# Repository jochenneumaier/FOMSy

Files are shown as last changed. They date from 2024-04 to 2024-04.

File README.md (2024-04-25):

# FOMSy
A 3D-Printed Flexible Open-Source Microfluidic System, containing a double syringe pump, pressure sensor and back pressure regulator

In this work, we introduce a low-cost open-source flow system that includes a dual syringe pump with implemented pressure sensor and back pressure regulator. The entire system can be built for around 500 €. Commercially available flow systems can be very expensive with equipment starting at, but often greatly exceeding, 10,000 €. This high price of entry makes such technology prohibitively expensive for many research groups. Such systems stand to benefit the emerging academic pharmaceutical field by providing the experience and availability of reliable and affordable solutions. To implement accessible flow chemistry at research facilities, the systems must be made affordable. In addition, space in research laboratories is usually limited and commercially available flow systems can be very bulky. Having a compact and individually adjustable system is thus beneficial, with 3D printing technology offering the solution. Our compact 3D-printed system meets the needs of many applications in flow chemistry research as well as educational requirements for universities. As a proof of concept, we conceptualized, developed, and tested a custom flow system that can be used to synthesize [18F]2-fluoro-2-desoxy-d-glucose ([18F]FDG), the most commonly used PET-tracer. This system was designed to perform the typical functions and operations required in radiotracer production i.e. radiofluorination, dilution, SPE-trapping, deprotection, and SPE-elution. With this proof-of-concept in hand, the system can be easily customized to produce other radiopharmaceuticals.

graphical abstract

The work was published in the Journal of Flow Chemistry and can be viewed here:

FOMSy: 3D-printed flexible open-source microfluidic system and flow synthesis of PET-tracer. F. Menzel, J. Cotton, T. Klein, A. Maurer, T. Ziegler, J. M. Neumaier, J. Flow Chem. 2023, https://doi.org/10.1007/s41981-023-00267-z

https://link.springer.com/content/pdf/10.1007/s41981-023-00267-z.pdf

A detailed assembly instructions can also be downloaded here:

https://static-content.springer.com/esm/art%3A10.1007%2Fs41981-023-00267-z/MediaObjects/41981_2023_267_MOESM1_ESM.pdf

All CAD and stl files as well as the Arduino and Nextion program codes can be downloaded here:

https://static-content.springer.com/esm/art%3A10.1007%2Fs41981-023-00267-z/MediaObjects/41981_2023_267_MOESM2_ESM.zip

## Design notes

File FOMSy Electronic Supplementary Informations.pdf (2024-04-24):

## Electronic Supplementary Informations

## FOMSy: 3D-Printed Flexible Open-Source Microfluidic System and Flow Synthesis of PET-Tracer

Florian Menzela,b, Jonathan Cottonb,c, Thomas Kleina

, Andreas Maurerb,c, Thomas Zieglera and Jochen M. Neumaier*a

a
Institute of Organic Chemistry, University of Tuebingen, Auf der Morgenstelle 18, 72076 Tuebingen, Germany.
b | Werner Siemens Imaging Center, Department of Preclinical Imaging and Radiopharmacy,
| Eberhard Karls University, Tuebingen, Roentgenweg 15, 72076 Tuebingen, Germany
c | Cluster of Excellence iFIT “Image-Guided and Functionally Instructed Tumor Therapies“
| (EXC 2180), University of Tuebingen, 72076 Tuebingen, Germany

*E-Mail: jochen.neumaier@uni-tuebingen.de

Table of contents

3D printer setup

Two 3D printers were used for this work. 3D-printed parts out of PLA (polylactic acid) and

PETG (polyethylene terephthalate glycol-modified) were printed on an X-CF Pro from Qidi. 3D-

printed parts out of PEEK (Polyetheretherketone) were printed on an Apium P220 from Apium

Additive Technologies GmbH.

Software: All parts were designed with Autodesk Inventor Professional 2022. After modeling,

the files were exported as STL files and sliced with the software simplify3D.

PEEK parts: The parts out of PEEK were printed with Apium PEEK 4000 Natural filament with

an Apium P220 3D printer. The filament roll was dried in a vacuum oven at 80 °C and 50 mbar

overnight to ensure proper drying of the PEEK.

Print speed = 25 mm/s

Extrusion width: 0.40 mm

Extrusion multiplier = 0.90

Nozzle temp. = 480 °C

Bed temperature = 130 °C, glass plate coated with DimaFix pen with a brim of 24 perimeters

Layer height: 0.1 mm

PLA parts: PLA 1.75 mm from Janbex was used on the Qidi X-CF Pro 3D printer.

The following settings were used:

Print speed = 60 mm/s

Extrusion multiplier = 1.00

Nozzle temp. = 200 °C

Bed temperature = 60 °C, printed on a flexible metal PEI sheet, coated with DimaFix Spray or

pen.

Layer height: 0.2 mm – 0.3 mm

PETG parts: PETG 1.75 mm from Fiberlogy was used on the Qidi X-CF Pro 3D printer. The

filament roll was stored in a sealed box with silica gel bags inside to ensure proper drying of

the PETG.

The following settings were used:

Print speed = 60 mm/s

Extrusion multiplier = 1.00

Nozzle temp. = 230 °C

Bed temperature = 80 °C, printed on a flexible metal PEI sheet, coated with DimaFix Spray or

pen.

Layer height: 0.2 mm (if a part was printed with 0.3 mm layer height, it is indicated in the parts

list)

The STP and STL files of all printed parts can be found in the zip file “Data Files” in the

supplementary information. For more information also see our previous publications. [1], [2]

Dual syringe pump

All 3D-printed parts were printed in PLA (black) and PETG (bordeaux red). The exploded-view

CAD drawing of the syringe pump can be found in Figure S1, the single parts in Figure S2, and

the full parts list in Table S1.

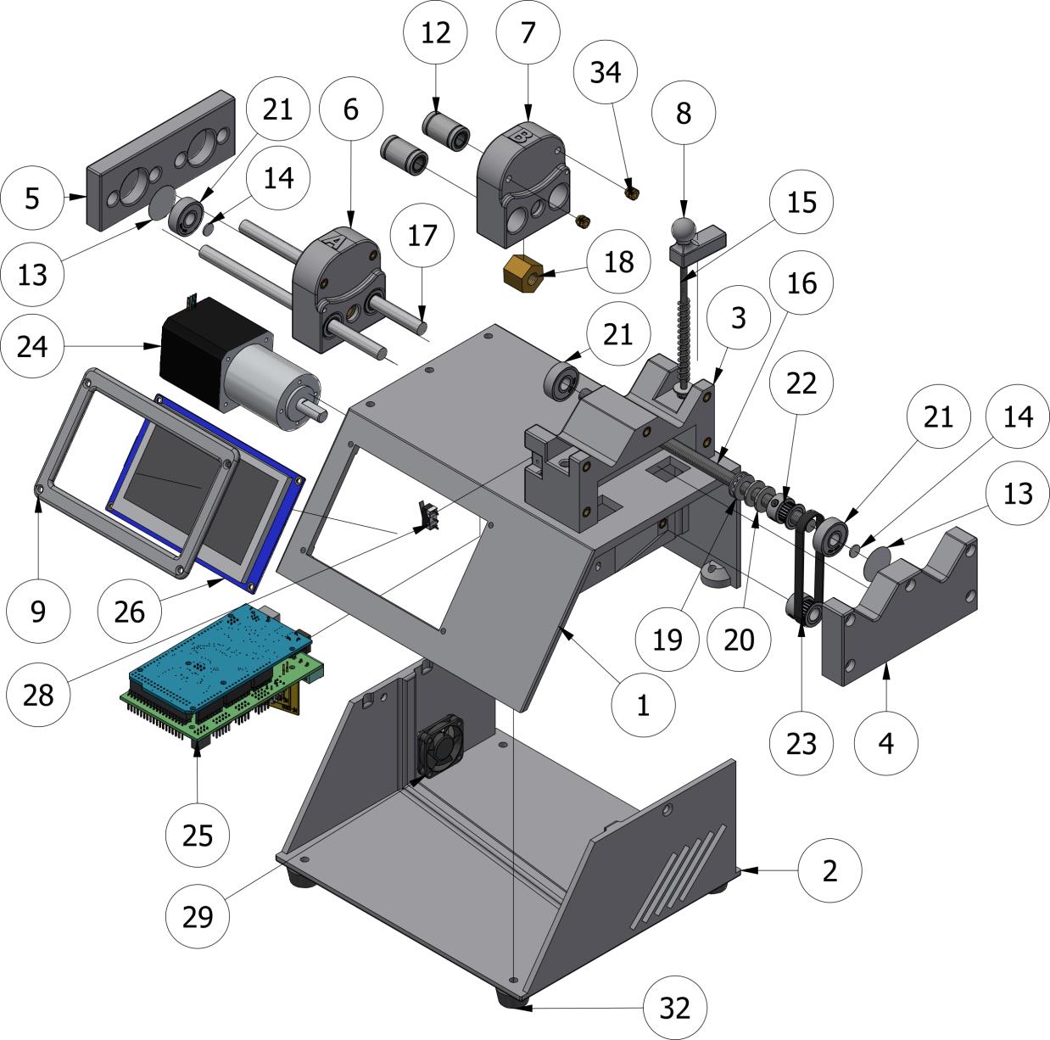
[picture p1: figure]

Figure S1: Exploded-view CAD drawings of the syringe pump.

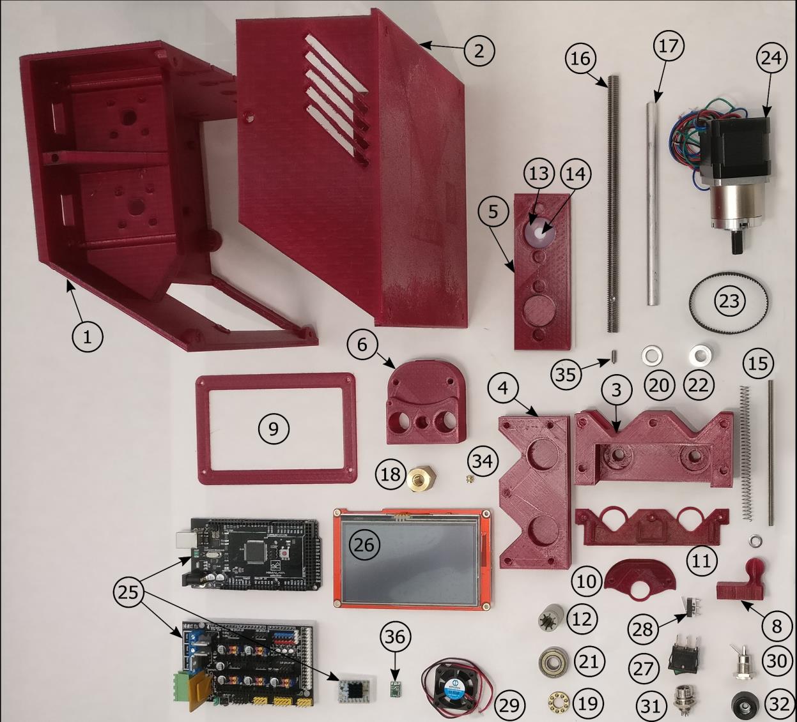
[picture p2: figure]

Figure S2: All 3D-printed, mechanical, and electronic parts with numbers.

Table S1: Parts list for the syringe pump. The screws and nuts that are needed for mounting

each part are given in brackets.

Quant. | Part | Source | No.
1 | Main pump body (printed with 0.3 mm layer height) | 3D-printed | 1
1 | Bottom part (printed with 0.3 mm layer height) | 3D-printed | 2
1 | Syringe holding block | 3D-printed | 3
1 | Front plate | 3D-printed | 4
1 | End plate | 3D-printed | 5
1 | Carrier block A | 3D-printed | 6
1 | Carrier block B | 3D-printed | 7
1 | Syringe clamp | 3D-printed | 8
1 | Display frame | 3D-printed | 9

Quant. | Part | Source | No.
2 | Syringe retainer back | 3D-printed | 10
1 | Syringe retainer front | 3D-printed | 11
4 | RJ4JP-01-08 drylin® R - bearing 8mm | Amazon | 12
4 | PTFE washer (22 mm × 0,1 mm) | In-house workshop | 13
4 | PTFE washer (8 mm × 2 mm) | In-house workshop | 14
2 | M4 Threaded rod | In-house workshop | 15.1
2 | compression spring 45 × 7 mm × 0.6 mm | In-house workshop | 15.2
2 | M4 locknut and washer, 12 mm | In-house workshop | 15.3
2 | Trapezoidal thread spindle, Tr8 × 1.5 × 185 mm | HFB-Gewindetechnik | 16
4 | Round rod, stainless steel, 8 × 145 mm | In-house workshop | 17
2 | Hexagon nut, Tr8 × 1.5 | HFB-Gewindetechnik | 18
2 | Thrust bearing, F8-16M 8 × 16 × 5mm | Amazon | 19
4 | Washer 8×16×15mm | In-house workshop | 20
6 | Ball bearing 608RS | Amazon | 21
4 | GT2 timing pulley, 8 mm bore, 20 teeth, for 6 mm belt | Amazon | 22
F4 | GT2 closed loop timing belt, 6 mm, 158 mm | Amazon | 23
2 | Nema 17 Stepper Motor Bipolar L=40mm w/ Gear Ratio 27:1 Planetary Gearbox | stepperonline | 24
1 | HIMALAYA basic MEGA 2560 | Eckstein GmbH | 25.1
1 | Ramps 1.4 controller | Eckstein GmbH | 25.2
3 | TMC2208 V1.2 stepper motor driver | Eckstein GmbH | 25.3
1 | Nextion NX4827T043 Display | Antratek Electronics | 26
1 | Rocker switch, 3-Pin | Eckstein GmbH | 27
2 | Pololu mini snap-action switch with 13.5mm lever | Eckstein GmbH | 28
1 | Cooling fan (30 × 30 × 10 mm), 5 V | Amazon | 29
1 | DC-socket 2.1/5.5mm | Reichelt elektronik GmbH & Co. KG | 30
1 | GX12 aviation socket, Pins 5 or 6 (+ aviation plug on the cable) | Amazon | 31
4 | Rubber feet, 20 × 9 mm | Amazon | 32
| Threaded inserts M4 × 8 or M4 × 6 | Amazon | 33
| Threaded inserts M3 × 6 | Amazon | 34
2 | Grub screw, M4 ×10 mm (ISO 4027) | In-house workshop | 35
1 | Pololu 5V Step-Up/Step-Down Voltage Regulator S9V11F5 | Eckstein GmbH | 36
| Hex Socket Head Cap Screws (ISO 4762), various sizes | In-house workshop | 37

Quant. | Part | Source | No.
| Hexagon socket countersunk screws (ISO 10642), various sizes | In-house workshop | 38
1 | Single output power supply 12 V, 3 A | Reichelt elektronik GmbH & Co. KG | 39
| jumper wire cables, female to female | Eckstein GmbH

Detailed step-by-step assembly instruction
In the following, a detailed assembly instruction with example photos is given. Together with

the exploded CAD view, it should be possible to assemble the pump without using special

tools. A bench drill with a vise is recommended in step 11 to drill an accurate hole.

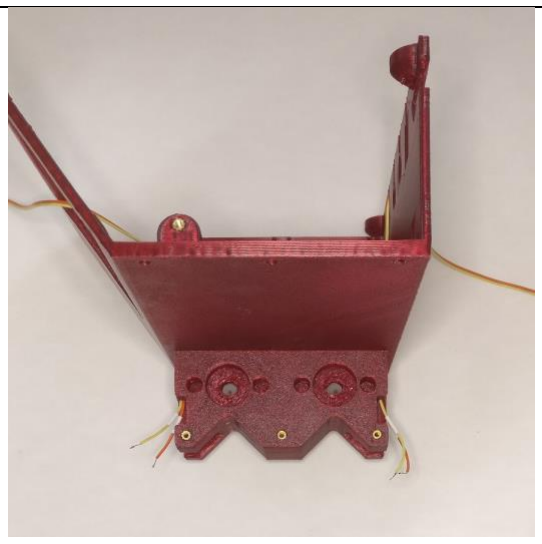
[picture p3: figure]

Step 1: All Threaded inserts (33 and 34) were inserted using a soldering iron Step 2: The two core wires for the end switch were pulled through the main pump body (1) and the syringe holding block (3). Step 3: The syringe holding block (3) was screwed (M4 head cap screws) on the main pump body (1).

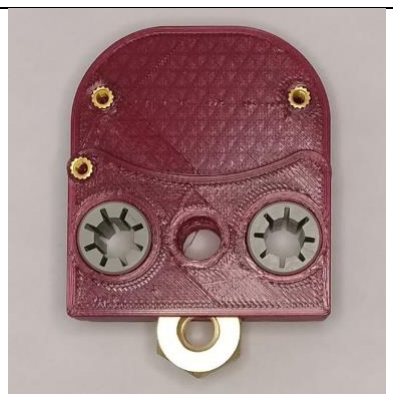
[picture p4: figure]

Step 4: The linear bearing (12) and the nut (18) were inserted into the carrier blocks A and B (6 and 7). Care should be taken that the round rod (17) runs without friction through the linear bearing! If not, increase the hole size of the carrier block.

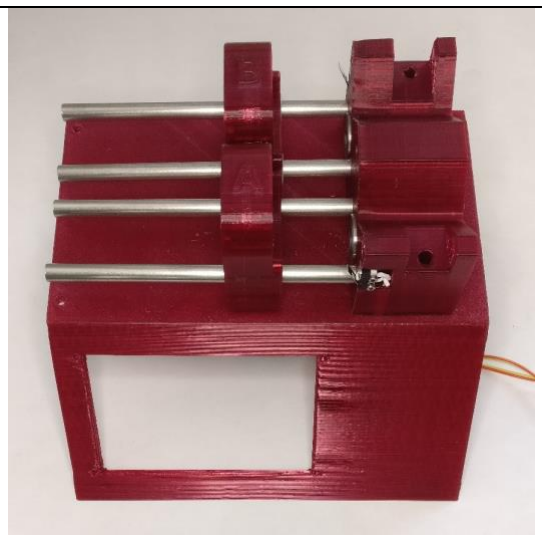
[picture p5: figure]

Step 5: The end switches (28) were soldered to the wires and attached to the syringe holding block. Step 6: The round rod (17) and two ball bearings (21) were inserted into the syringe holding block (3). Step 7: The two carrier blocks A and B (6 and 7) were slid in the round rods.
Step 8: The two 22 mm PTFE washers (13) and the two ball bearings (21) were inserted in the end plate (5). Step 9: The two 8 mm PTFE washers (14) were inserted into the two ball bearings (21).

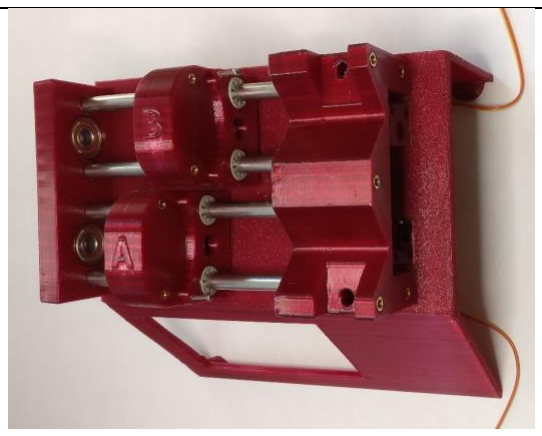
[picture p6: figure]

Step 10: The end plate (5) was screwed (M4 head cap screws) to the main pump body (1). Care should be taken that the carrier blocks move without friction!

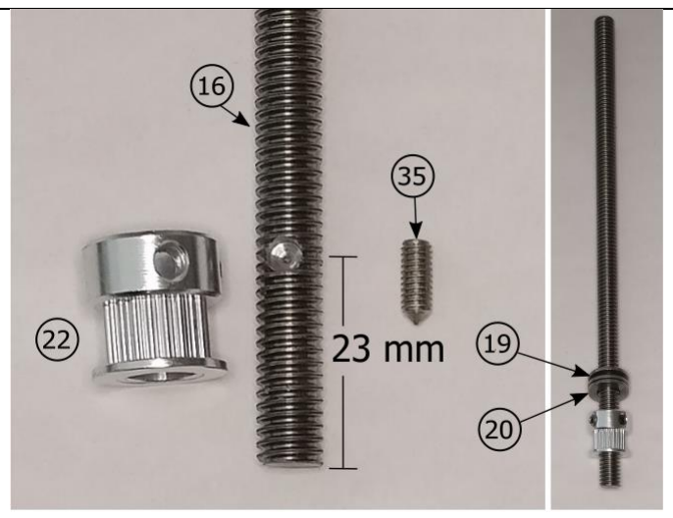
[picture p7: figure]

Step 11: A hole (4mm) was drilled halfway through the trapezium thread spindle (16) with a distance of 23 mm from center to end (bench drill with a vise is recommended). Step 12: The timing pulley (22) was screwed to the threaded spindle with a grub screw (35). Step 13: Two washers (20) and the thrust bearing (19) were attached (total thickness of 8mm).

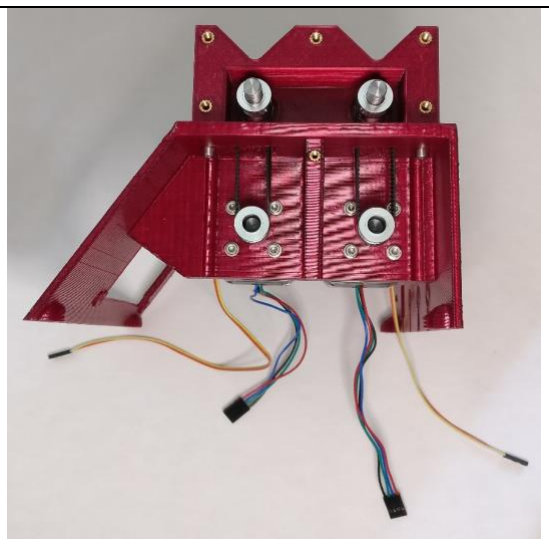
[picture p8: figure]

Step 14: The spindles from step 13 were inserted. Make sure that the spindle can be rotated without much resistance! Step 15: The gear stepper motors (24) were loosely attached (M3 head cap screws with washers) to the main pump body (1). Step 16: The timing pulleys (22) and the timing belts (23) were attached. The timing belts were put under tension and the motors and pulleys were tightened firmly.

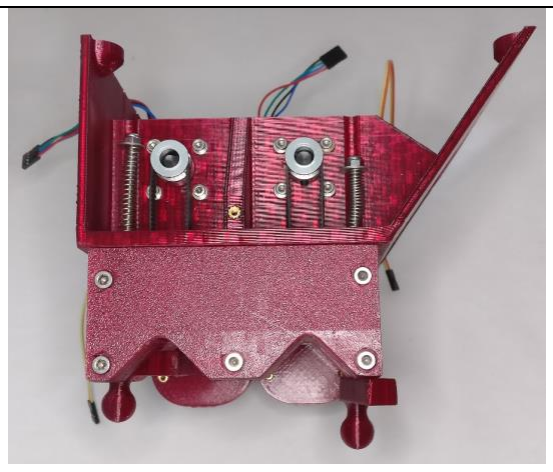
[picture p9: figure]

Step 17: The front plate (4) was screwed (M4 head cap screws) to the pump. Step 18: The M4 threaded rods (15.1) were screwed into the syringe clamps (8) and inserted through the holes. Step 19: The compression spring (15.2) was inserted and fixed with the washer and lock nut.
Step 20 (optional): A second 5 V output was soldered to the Voltage Regulator (36). This could be used to supply power to the sensor module if no motorized BPR is used! If a separate power supply on the sensor module is used, do not connect power from pump to sensor!

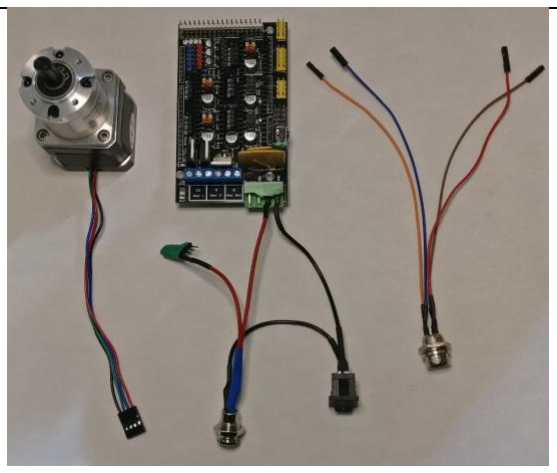
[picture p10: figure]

Step 21: The cables of the motors were shortened and connected to a 4-pin plug (black – green – blue – red). Step 22: Cables were soldered (see figure S3) to the components (27, 30, 31, 36). The 12 V (+ and -) input cable was soldered directly to the RAMPS controller (25.2) The voltage regulator (36) should be encased in heat shrink tubing to prevent accidental electrical contact with other parts.

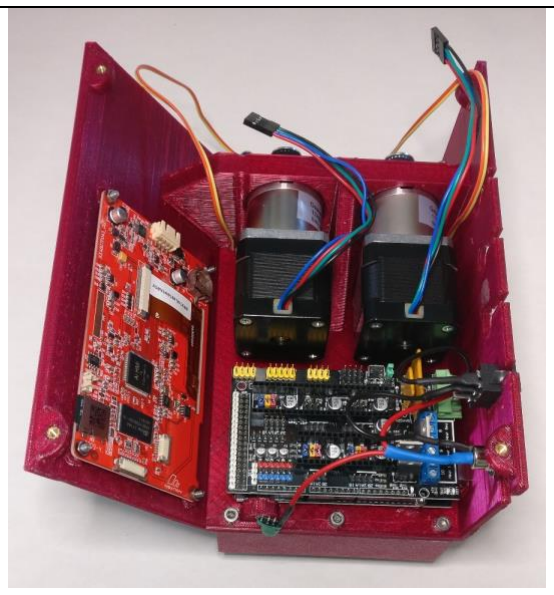
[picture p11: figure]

Step 23: The Arduino Mega (25.1) was screwed (M3 head cap screws) to the Main pump body (1). Step 24: The electronic part from step 22 was attached to the main pump body. The RAMPS controller (25.2) was plugged on the Arduino. Step 25: The Nextion display (26) was screwed (M3 countersunk screws with M3 nuts) with the display frame (9) to the main pump body.
Step 26: The TMC2208 stepper motor drivers (25.3) were plugged on the RAMPS (Jumper to MS2, middle position). Step 27: The wires were connected as described in Figure S3.
Step 28: The cooling fan was screwed (M3 countersunk screws with M3 nuts) to the bottom part (2)

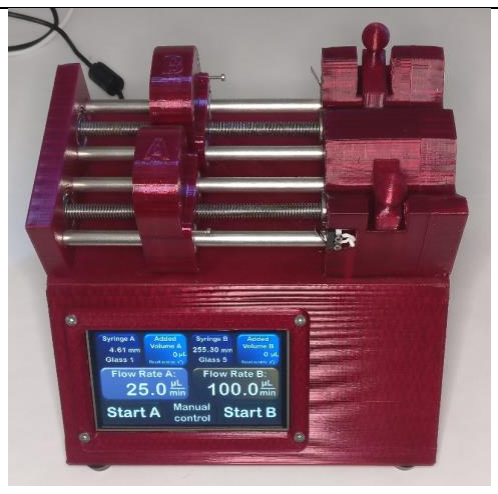
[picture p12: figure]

Step 29: The bottom part (2) with the rubber feet (32) was screwed (M3 countersunk and head cap screws) to the main pump body (1). PLA version of the pump:

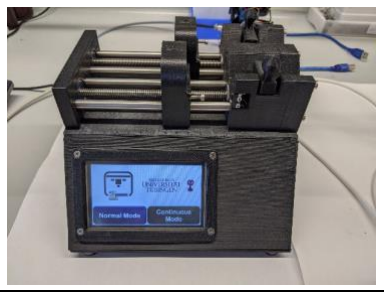
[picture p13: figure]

Optional: Syringe retainers (10 and 11) can be used to hold the syringes in place when drawing up a solution into the syringe using the motors.
The syringe retainers must be adjusted for each syringe itself so that it fits optimally (change hole diameter and thickness).
The uploaded retainers are optimized for a Hamilton 5 mL Gastight Syringe Model 1005

Electronic setup of the pump
For controlling the motors of the pump an Arduino Mega 2560 was used with a RAMPS 1.4

controller shield attached. TMC2208 stepper motor driver was connected to the RAPMS

controller at X and Y positions and the jumper settings were set to 1/4 microsteps (jumper on

MS2, middle position). The current limiting was adjusted on the TMC2208 stepper motor

driver to around 2.4 A with the integrated trimmer potentiometer (1.2 V). For a constant

voltage of 5 V for the Nextion Display, a Pololu S9V11F5 5 V Step-Up/Step-Down Voltage

Regulator was used. The RAMPS controller was connected to a standard 12 V DC, 3 A power

supply over a rocker switch, and a DC socket. The detailed assignment of the electronics is

shown in Figure S3. All electronic parts were connected using standard female-to-female or

female-to-male jumper wires.

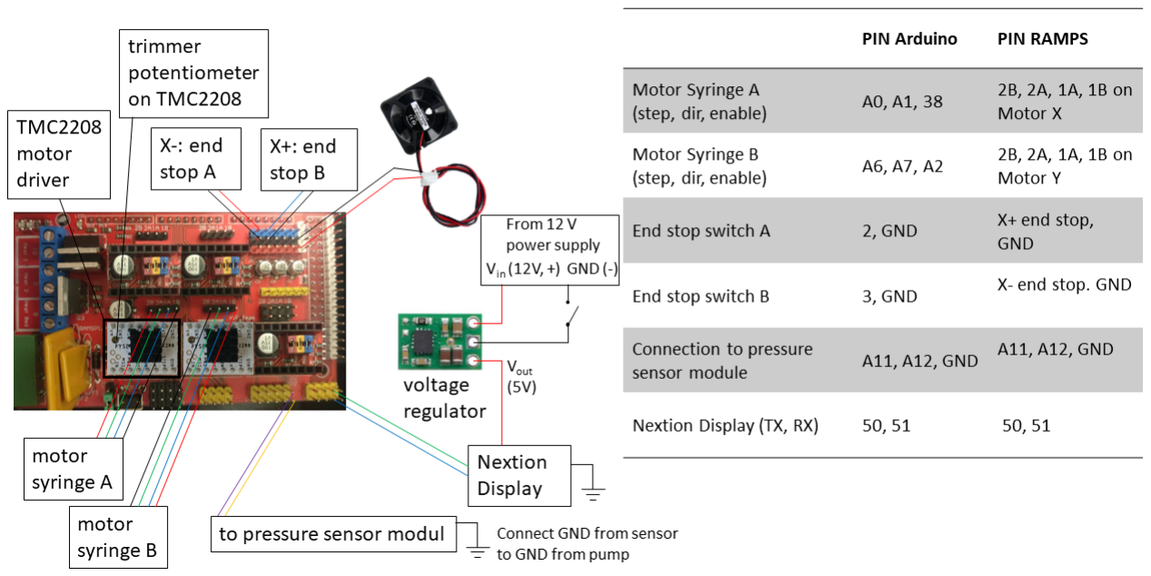
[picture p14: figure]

Figure S3: Wiring diagram of the Arduino with PIN assignment.

Programming with Arduino and Nextion software: The software was written on the open-

source Arduino software (Ver. 1.8.15) and the Nextion Editor (Ver. 1.63.3.). The codes can be

downloaded from the supplementary files. In the software, five Hamilton gastight syringes

and five disposable syringes were implemented. The diameters of these syringes were taken

from the corresponding company’s website. Detailed Information (company, diameter,

accuracy) can be found in Table S2. For changing the syringes to other predefined syringes,

the Nextion code on pages “syA” and “syB” has to be edited. The text in the buttons b0 – b9

could be changed to the corresponding value in the attribute window (change txt). The

diameter of new syringes has to be edited in the event window. An example is given here:

Old syringe | New syringe | Changes

n1.val=4

t13.txt="69"

main.t5.txt="Plastic 1"

n1.val=6

t13.txt="12"

main.t5.txt="Metal 1"

The diameter was changed from 4.69 mm

to 6.12 mm. The name, which appears on

the main page, was changed from Plastic

1 to Metal 1.

Accuracy test of the syringe pump: Each kind of pre-programmed syringes were tested with

typical flow rates for continuous flow reactions. Distilled water was dispensed at room

temperature for 1 to 10 min and the measured weight was compared to the theoretical

weight.

Table S2: Accuracy test of the pre-programmed syringes.

Volume | Syringe | Flow rate [µL/min] | Time [min] | Weight [g] | Deviation [%]
1 mL | HSW NORM-JECT® | 100 50 10 5 1 | 5 10 20 30 50 | 0.498 0.497 0.197 0.147 0.048 | 0.08 0.29 1.52 1.78 3.47

Volume | Syringe | Flow rate [µL/min] | Time [min] | Weight [g] | Deviation [%]
2 mL | BD Discardit II | 200 100 20 10 2 | 5 10 20 30 50 | 0.995 0.995 0.397 0.295 0.098 | 0.27 0.30 0.42 1.54 2.09
5 mL | BD Discardit II | 500 250 50 25 5 | 5 10 20 30 50 | 2.474 2.481 0.993 0.737 0.243 | 0.81 0.50 0.44 1.56 2.53
10 mL | HSW NORM-JECT® | 1000 500 100 50 10 | 5 10 20 30 50 | 4.970 4.961 1.987 1.474 0.488 | 0.34 0.53 0.40 1.48 2.18
20 mL | BD Discardit II | 2000 1000 200 100 20 | 5 10 20 30 50 | 9.897 9.913 3.972 2.928 0.973 | 0.78 0.62 0.46 2.21 2.49
0.1 mL | Hamilton Gastight 1710 | 10 5 1 0.5 0.1 | 5 10 20 30 50 | 0.049 0.049 0.019 0.014 0.005 | 0.04 0.45 0.85 5.26 10.71
0.25 mL | Hamilton Gastight 1725 | 25 12.5 2.5 1.25 0.25 | 5 10 20 30 50 | 0.125 0.124 0.049 0.036 0.012 | 0.04 0.20 2.73 2.94 5.55

Volume | Syringe | Flow rate [µL/min] | Time [min] | Weight [g] | Deviation [%]
1 mL | Hamilton Gastight 1001 | 100 50 10 5 1 | 5 10 20 30 50 | 0.498 0.498 0.197 0.147 0.048 | 0.00 0.10 1.26 1.54 4.01
2.5 mL | Hamilton Gastight 1002 | 250 125 25 12.5 2.5 | 5 10 20 30 50 | 1.245 1.245 0.498 0.373 0.123 | 0.06 0.08 0.12 0.26 1.51
5 mL | Hamilton Gastight 1005 | 500 250 50 25 5 | 5 10 20 30 50 | 2.475 2.480 0.993 0.737 0.243 | 0.67 0.44 0.31 1.46 2.35
10 mL | Hamilton Gastight 1010 | 1000 500 100 50 10 | 5 10 20 30 50 | 4.970 4.961 1.970 1.475 0.488 | 0.24 0.43 1.16 1.32 2.01
25 mL | Hamilton Gastight 1025 | 2500 1250 250 125 25 | 5 10 20 30 50 | 12.397 12.413 4.971 3.728 1.221 | 0.47 0.34 0.22 0.24 2.01

Table S3: Accuracy test of the pre-programmed syringes at 5 bar (PETG system).

Volume | Syringe | Flow rate [µL/min] | Time [min] | Weight [g] | Deviation [%]
1 mL | Hamilton Gastight 1001 | 50 5 | 10 30 | 0.493 0.146 | 1.16 2.30
10 mL | Hamilton Gastight 1010 | 1000 100 | 5 20 | 4.965 1.968 | 0.35 1.27

Table S4: Accuracy test of the pre-programmed syringes at 5 bar (PLA system).

Volume | Syringe | Flow rate [µL/min] | Time [min] | Weight [g] | Deviation [%]
1 mL | Hamilton Gastight 1001 | 50 5 | 10 30 | 0.494 0.146 | 0.96 2.16
10 mL | Hamilton Gastight 1010 | 1000 100 | 5 20 | 4.961 1.969 | 0.42 1.22

Pressure Sensor

The case for the electronic component was printed in PETG (bordeaux red). For our

applications, the solvent touching part No. 40 was printed out of PEEK, but other materials

such as PP or PVDF are also possible. The exploded-view CAD drawing of the pressure sensor

case and the sensor can be found in Figure S4, and the part numbers can be found in Table

S5.

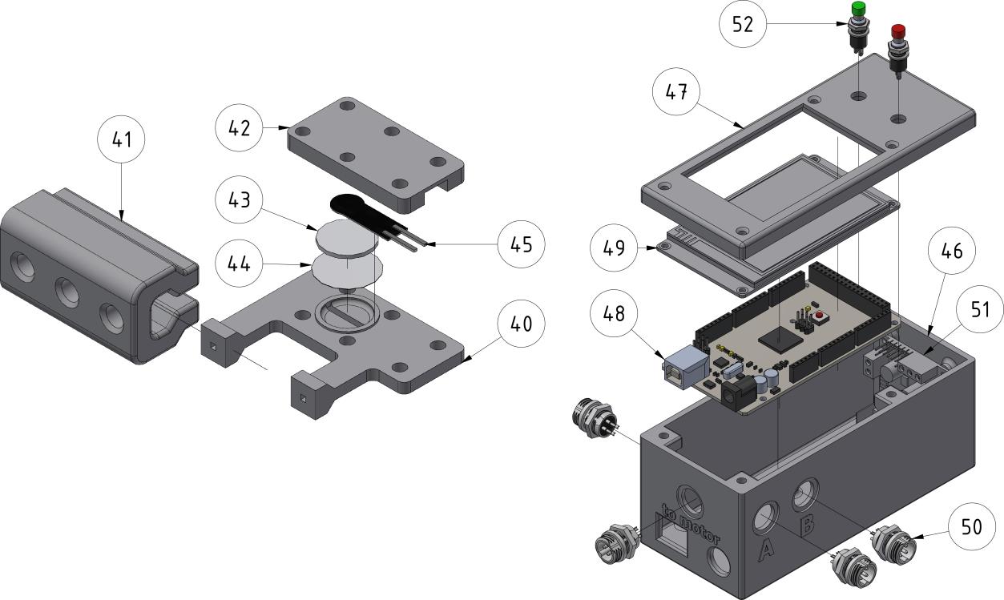
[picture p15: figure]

Figure S4: Exploded-view CAD drawings of pressure sensor and case.

As described in our latest publication,[2] the flat side of the sensor, on which the flat bottom

1/4″-28 fitting is pressed, was sanded with 220 – 1500 grit abrasive paper to ensure a smooth

surface and a leakproof connection. The ring, upon which the septum is placed, was sanded

the same way.

Table S5: Part list for the sensor case and the sensor. The screws and nuts that are needed for

mounting each part are given in brackets.

Quant. | Parts Sensor and case | Source | No.
1 | Pressure sensor main body (printed with 0.1 mm layer height) | 3D-printed | 40
1 | Guide rail | 3D-printed | 41
1 | Pressure sensor lid | 3D-printed | 42
1 | Silicone disc, 14 mm diameter, 1 mm thickness | In-house workshop | 43
1 | PTFE disc, 16 mm diameter, 0.1 mm thickness | In-house workshop | 44
1 | Force sensing resistor, 0 – 10 kg, 9 × 0.25 mm | Amazon | 45
1 | Electronic case | 3D-printed | 46
1 | Electronic case lid | 3D-printed | 47
1 | HIMALAYA basic MEGA 2560 | Eckstein GmbH | 48
1 | Nextion NX4832T035 Display | Antratek Electronics | 49

Quant. | Parts Sensor and case | Source | No.
3 | GX12 aviation socket, Pins 5 or 6 (+ aviation plug on the cable) | Amazon | 50
1 | L298N Motor Drive Controller | Amazon | 51
2 | Push button switch, 6 mm hat diameter | Amazon | 52
| jumper wire cables, female to female | Eckstein GmbH | 53
1 | Optional: pressure gauge holder | 3D-printed | 54
1 | Optional: manometer Cl 2.5 from WIKA with an O-Ring 10 × 2.5 mm | WIKA | 55

Detailed step-by-step assembly instruction
In the following, a detailed assembly instruction with example photos is given. Together with

the exploded CAD view, it should be possible to assemble the pressure sensor without using

special tools.

Step 1: The flat sides (marked with an arrow) of the pressure sensor main body (40) were sanded with 220 – 1500 grit abrasive paper to ensure a smooth surface.

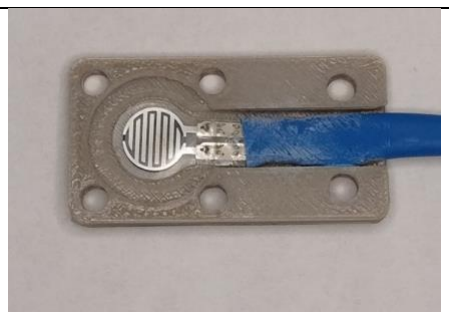
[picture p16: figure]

Step 2: The force sensing resistor (44) was soldered to a two-core wire and sealed with heat shrink tubing. Step 3: The force sensing resistor (44) was glued in the pressure sensor lid (42) on the hose with super glue. Do not use superglue under the sensor plate!
Step 4: The silicone disc (43) was inserted
Step 5: The M3 head cap screws and the PTFE disc (44) were inserted.

Step 6: The pressure sensor main body (40) was carefully applied to the prepared pressure sensor lid (step 5) without shifting the silicone disc and screwed on it (M3 nuts and washers).

Back pressure regulator (BPR)

The exploded-view CAD drawing of two variations of the BPR can be found in Figure S5 and

the part numbers can be found in Table S6. The STP and STL files of all printed parts can also

be found in the supplementary download file. As for the pressure sensor, the flat side and the

ring in the middle of the BPR were sanded with 220 – 1500 grit abrasive paper to ensure a

smooth surface and a leakproof connection. For our applications, the solvent touching part

No. 56 was printed out of PEEK, but other materials such as PP or PVDF are also possible.

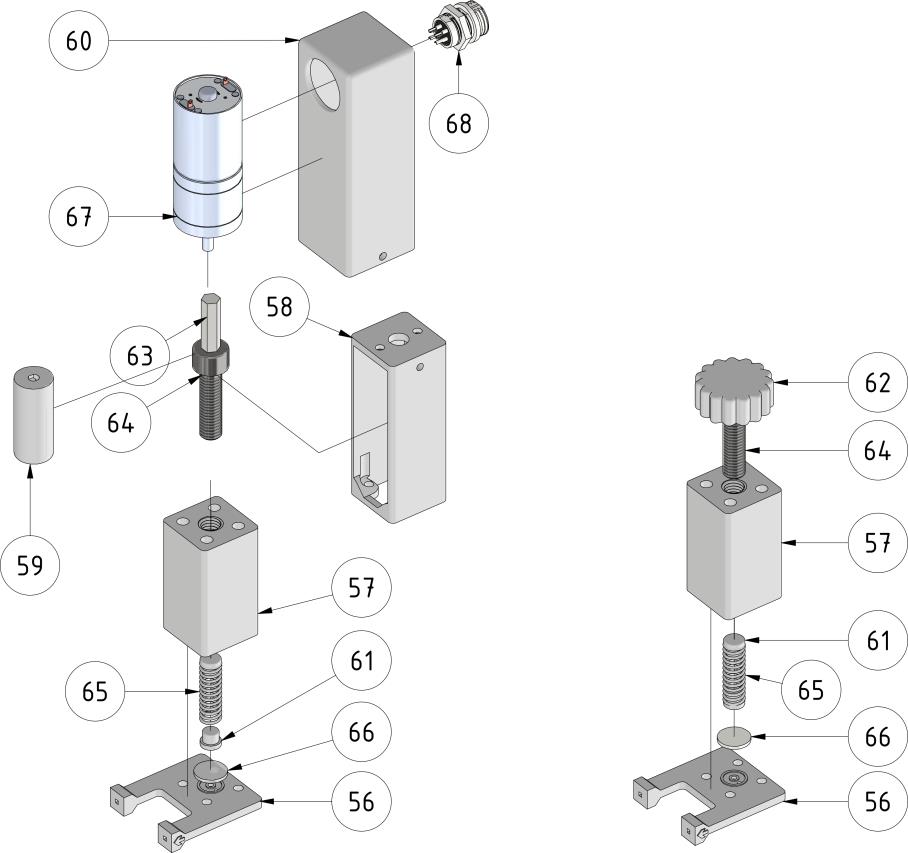
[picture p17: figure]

Figure S5: Exploded-view CAD drawings of the motor-controlled BPR and the manual-

controlled BPR.

Table S6 Parts list for the BPRs

Quant. | Parts spring pressured BPR | Source | No.
1 | BPR Main body (printed with 0.1 mm layer height) | 3D-printed | 56
1 | BPR top part | 3D-printed | 57
1 | Motor mount | 3D-printed | 58
1 | Motor shaft coupler | 3D-printed | 59
1 | Motor cover | 3D-printed | 60
2 | Spring cap | 3D-printed | 61
1 | M8 press-fit head | 3D-printed | 62
1 | 6 mm hexagonal rod (25 mm) | In-house workshop | 63
1 | Cheese head screw with hexagon socket, M8 × 30 mm) | In-house workshop | 64
1 | Spring 1.0 × 8 × 25 mm | IVO Industriebedarf | 65
1 | Septum 12 mm, PTFE red/Silicone white, 1 mm thickness | Sigma-Aldrich | 66
1 | 12 V DC gear motor, 25mm, 10 rpm | Amazon | 67
1 | GX12 aviation socket, Pins 5 or 6 (+ aviation plug on the cable) | Amazon | 68

Detailed step-by-step assembly of the motor-controlled BPR
In the following, a detailed assembly instruction with example photos is given. Together with

the exploded CAD view, it should be possible to assemble the pressure sensor without using

special tools.

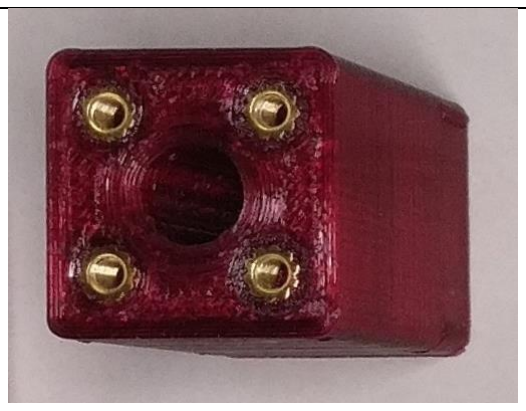
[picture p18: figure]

Step 1: All threaded inserts (M6, Pos. 34) were inserted into the BPR top part (57) using a soldering iron

Step 2: The flat sides (marked with an arrow) of the BPR main body (56) were sanded with 220 – 1500 grit abrasive paper to ensure a smooth surface.

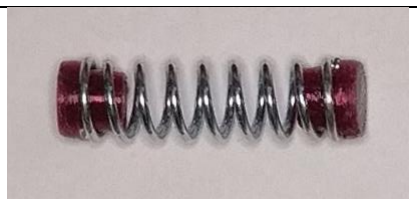
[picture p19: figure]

Step 3: Spring caps (61) were inserted into the spring (65).
Step 4: The Septum (66) was inserted. Red side (PTFE) facing to the bottom part, white side facing (silicone) to the spring cap Step 5: The spring with caps from step 3 was inserted.

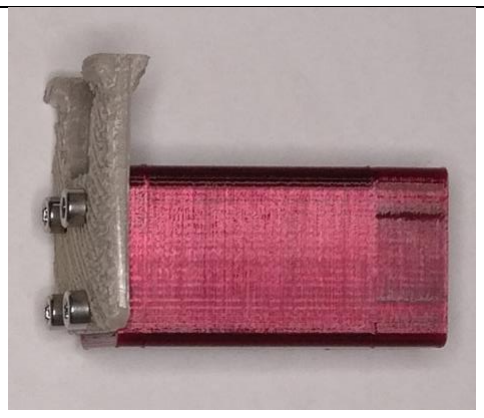
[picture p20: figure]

Step 6: The BPR main body (56) was carefully applied to the prepared BPR top part (57) without shifting the septum and screwed on it (M3 nuts and washers).
Step 7: The hexagonal rod (63) was glued into the cheese head screw with hexagon socket, M8 × 30 mm (64) using super glue.
Step 8: The prepared M8 screw from step 7 was screwed into the BPR top part from step 6. Prior retapping of the thread with an M8 tap may be necessary.

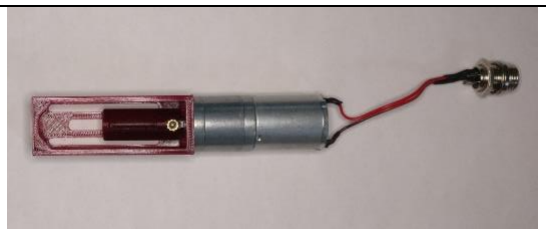
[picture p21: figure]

Step 9: The aviation socket (68) was soldered to the gear motor (67). Step 10: The gear motor (67) was screwed to the motor mount (58) and the motor shaft coupler was inserted (with M4 × 6 threaded insert and an M4 grub screw).
Step 11: The prepared motor mount from step 9 was screwed to the BPR top part from step 8. Step 12: the motor cover was screwed to the motor mount and the aviation socket was fixed to the motor cover through the hole.

To assemble the manually controlled BPR, follow steps 1 - 6. Instead of gluing the hexagonal rod onto the M8 screw, press the M8 press-fit head (62) into the screw using a vise.

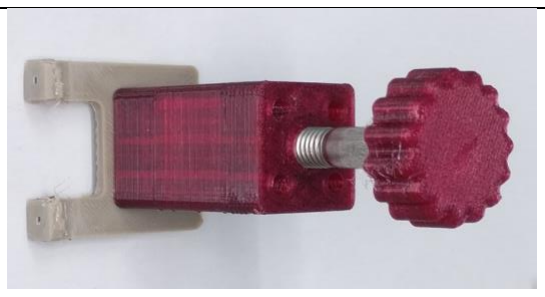
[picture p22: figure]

Electronic setup of the sensor and BPR
For controlling the pressure sensor an Arduino Mega 2560 was used. The motor of the BPR

was controlled with an L298N motor drive controller using 12 V from the power source. For a

constant voltage of 5 V for the Nextion Display, a step-up/step-down voltage regulator was

used. The Arduino was connected directly to a standard 12 V DC, 3 A power supply. The L298N

and the voltage regulator were connected to 12 V using the Vin pin from the Arduino Mega.

The detailed assignment of the electronics is shown in Figure S6. All electronic parts were

connected using standard female-to-female or female-to-male jumper wires.

For the connector cables between the components, two core wires with aviation plugs were

used. To ensure correct signal transmission from the sensor to the pump, 10 kΩ resistors were

placed behind pins 7 and 8 respectively.

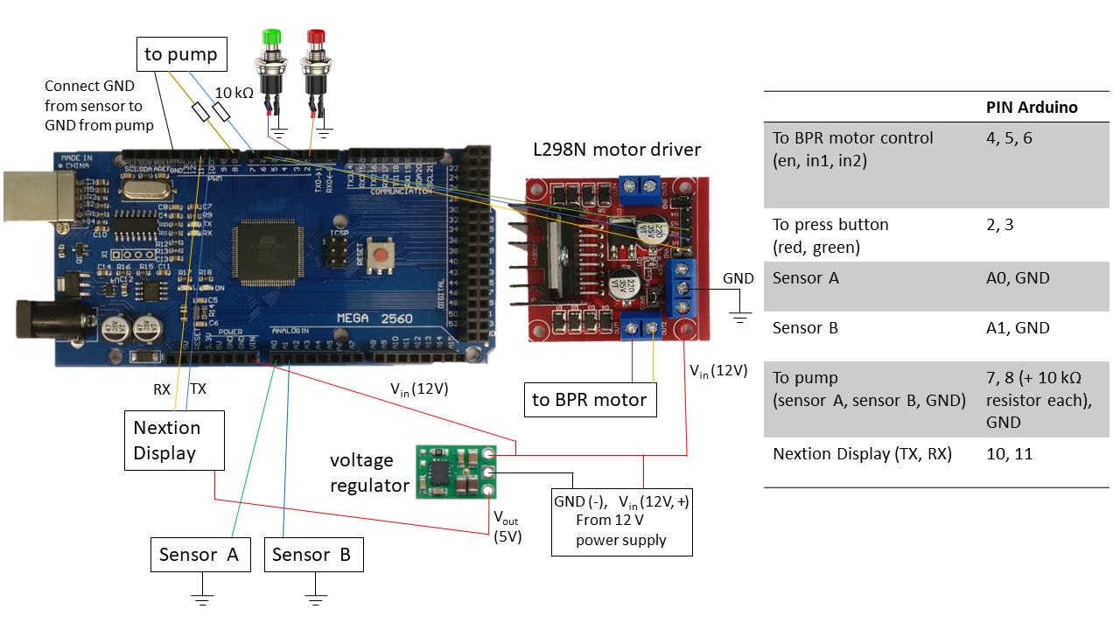
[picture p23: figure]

Figure S6: Wiring diagram of the pressure sensor and BPR with PIN assignment.

Calibration of the pressure sensor
For the calibration of the pressure sensor, the sensor was connected to a manometer (Cl 2.5

from WIKA (6 bar). The Arduino Mega has an 8-bit analog-to-digital converter (1024 data

points) that is used with the force-sensing resistor. 20 datapoints, ranging from 0.5 to 6 bar, were measured and the protocol from Kenji Ohgane[3] was used to perform a sigmoid plotting

of the data points. The excel table, which can be used for individual calibration, can also be

found as a supplementary file.

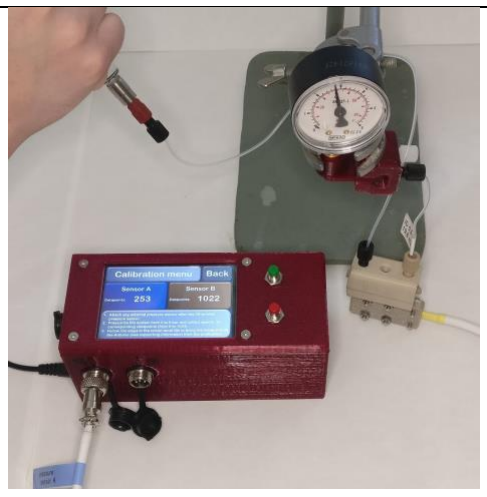
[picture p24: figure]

Step 1: The assembled sensor was connected to any external pressure sensor using the guide rail (41) with 1/4-28 flat-bottom fitting (IDEX H&S XP-230) and 1/16’’ ETFE tubing. Here, we use the pressure gauge holder
(54) with a monometer (Cl 2.5 from WIKA) (55) sealed by an O-ring. The cable from the sensor was connected to the electronic case (sensor A/B).
Step 2: Pressurize the system from 0 to 6 bar and collect approx. 20 corresponding data points (from 0 to 1024)
Step 3: Open the solver excel file and follow the steps in the excel file to bring the data points to the Arduino (the excel file can be found in the supporting information)

Step 4: Follow the instructions in the excel file:
(1) Paste the 8-bit data points and the measured pressure into columns G and H.
(2) Start Excel Solver (Tools > Solver)
(3) Set "Target cell" to "B7" (Sum of squared residuals).
(4) Click "Solve" to perform the fitting.
(5) Close the solver window and check the graph to see if the calculated curve fitted well.
(6) go to sheet "switch case - one line"
(7) copy the value of C1 to the Arduino software (line 364 for sensor A, line 372 for sensor B). Make sure to have "." as a decimal separator

Notes and references

[1] Neumaier JM, Madani A, Klein T, Ziegler T (2019) Low-budget 3D-printed equipment for continuous flow reactions. Beilstein J. Org. Chem. 15:558–566. https://doi.org/10.3762/bjoc.15.50
[2] Menzel F, Klein T, Ziegler T, Neumaier JM (2020) 3D-printed PEEK reactors and development of a complete continuous flow system for chemical synthesis. React. Chem. Eng. 5:1300-1310. https://doi.org/10.1039/D0RE00206B
[3] Ohgane K (2019) Sigmoid fitting in Excel (Excel Solver Add-In), protocols.io, https://doi.org/10.17504/protocols.io.78ihrue

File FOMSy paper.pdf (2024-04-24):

Vol.:(0123456789) 1 3

Journal of Flow Chemistry
https://doi.org/10.1007/s41981-023-00267-z

FULL PAPER

### FOMSy: 3D‑printed flexible open‑source microfluidic system and flow synthesis of PET‑tracer

Florian Menzel¹,2 | · Jonathan Cotton²,3 | · Thomas Klein¹ · Andreas Maurer²,3 | · Thomas Ziegler¹ ·
Jochen M. Neumaier¹

Received: 6 February 2023 / Accepted: 7 March 2023
© The Author(s) 2023

Abstract
In this work, we introduce a low-cost open-source flow system that includes a dual syringe pump with implemented pressure sensor and back pressure regulator. The entire system can be built for around 500 €. Commercially available flow systems can be very expensive with equipment starting at, but often greatly exceeding, 10,000 €. This high price of entry makes such technology prohibitively expensive for many research groups. Such systems stand to benefit the emerging academic pharmaceutical field by providing the experience and availability of reliable and affordable solutions. To implement accessible flow chemistry at research facilities, the systems must be made affordable. In addition, space in research laboratories is usually limited and commercially available flow systems can be very bulky. Having a compact and individually adjustable system is thus beneficial, with 3D printing technology offering the solution. Our compact 3D-printed system meets the needs of many applications in flow chemistry research as well as educational requirements for universities. As a proof of concept, we conceptualized, developed, and tested a custom flow system that can be used to synthesize [

18F]2-fluoro-2-desoxy-d-glucose ([¹⁸F]FDG), the most commonly used PET-tracer. This system was designed to perform the typical functions and operations required in radiotracer production i.e. radiofluorination, dilution, SPE-trapping, deprotection, and SPE-elution. With this proof-of-concept in hand, the system can be easily customized to produce other radiopharmaceuticals.
Keywords Flow chemistry · Chemical engineering · 3D printing · Radiochemistry · Open hardware

Introduction

Continuous flow chemistry has undergone rapid growth
over the last two decades [1–4]. Flow chemistry offers the unique benefits of improved mixing and heating efficiency as well as easy scale-up while reducing reaction time and solvent consumption [5–8]. Due to its beneficial properties, many applications for research and industrial organic synthesis have been developed. It can be combined with almost every technology, like photochemistry [9], catalysis [10], or electrochemistry [11]. One of the drawbacks is the prerequisite for expensive proprietary equipment that is not always affordable or obtainable. The combination of 3D printing and flow chemistry has emerged in recent years and could solve the hurdle of expensive equipment. Both, microreactors and various pump systems have already been described using 3D printing [12–19]. It can also be a useful tool for other sciences, printing various scientific devices such as microscopes, centrifuges, or 3D models for educational purposes [20].
One application in which the full potential of flow chemistry is utilized is the synthesis of radiopharmaceuticals and PETtracers [21–23]. This is mostly reliant on automation using expensive and proprietary equipment that is unobtainable to many researchers. To address this need, we developed an open-source 3D printed microfluidic system that can be produced for around 500 €. The system includes a dual syringe pump, a back pressure regulator (BPR) as well as a pressure sensor (PS). In combination with our 3D-printed microreactors,

* Jochen M. Neumaier
jochen.neumaier@uni-tuebingen.de
1 | Institute of Organic Chemistry, University of Tuebingen, Auf der Morgenstelle 18, 72076 Tuebingen, Germany
2 | Werner Siemens Imaging Center, Department of Preclinical Imaging and Radiopharmacy, Eberhard Karls University, Tuebingen, Roentgenweg 15, 72076 Tuebingen, Germany
3 | Cluster of Excellence iFIT “Image‑Guided and Functionally Instructed Tumor Therapies“ (EXC 2180), University of Tuebingen, 72076 Tuebingen, Germany

which were published in our previous work [14], the system can be customized to perform crucial radiosynthetic steps such as fluorination, dilution, and SPE (solid phase extraction) trapping/eluting. This system can be customized to rapidly produce a wide range of tracers and prosthetic radioligands with high molar activity and activity concentration, all within a small footprint. In this work, we evaluated this new system by synthesizing [

18F]2-fluoro-2-desoxy-d-glucose ([¹⁸F]FDG), the gold standard of PET radiotracers (Fig. 1).
[

18F]FDG is the most common and approved radiopharmaceutical for positron emission tomography (PET) and is used for non-invasive in vivo measurements of glucose metabolism [24]. Tumor cells, because of the Warburg effect, exhibit characteristically high glucose metabolism and can thus be differentiated from other normal tissue in PET by their high tracer uptake [25–27]. Lung cancer, brain cancer, lymphoma, melanoma as well as breast cancer are examples of cancer cells with higher glucose metabolism [28, 29]. [

18F]FDG is a structural analog of glucose and recognized by cells accordingly. After being transported via GLUT-1 and GLUT-3 into cells, it is phosphorylated by hexokinase to [

18F]FDG-6-phosphate.
This cannot be further metabolized and is thus trapped in the cell [30, 31]. Being deficient of neutrons, the radioactive ¹⁸F-isotope strives for a more stable energy state, which is achieved through a β⁺-decay. In this process a proton (p) decays into a neutron (n), emitting a positron (e⁺) and an electron neutrino (ν⁻
) [32]. The reaction can be described by the following equation.

The nucleon number in the nucleus remains the same, while the atomic number is decreased by the value of one. In the case of radioactive β⁺-decay of ¹⁸F, the stable oxygen isotope ¹⁸O is formed. Positrons are antiparticles of electrons and differ only by their sign. They dissipate kinetic energy by inelastic interactions with the tissue in the body and recombine with an electron present in the environment, forming a positronium exotic atom. In subsequent annihilation, the mass of the two particles converts into a pair of anti-parallel 511 keV gamma photons. These photons are simultaneously detected within a ring of scintillator detectors and a tomographical map of tracer accumulation (PET image) can be generated [33].
The synthesis of [

18F]FDG has already been excessively well described in the literature [23, 34, 35] and the GMP tracer is routinely produced in multi-patient doses from commercially available kits designed for expensive automated radiosynthesis

p → n + e+ + ν−

devices. The requirements and considerations for our custom system address several of the factors that play a role in typical diagnostic radiopharmaceutical production: (1) Due to the half-life of the ¹⁸F-Isotope (109.5 min) [36], the total reaction time, including all purification, should be as short as possible.
(2) Handling radioactive material should be as safe as possible. The transition to highly adaptable automated systems decreases the radiation exposure of the operator. (3) The reactions should be efficient and reproducible. The tracer precursors are expensive, and the amount used for each synthesis should be minimized. More so, the production of radioactive and chemical by-products should be minimized as their presence would require time-consuming purification by solid phase extraction (SPE) or HPLC. (4) Furthermore, the system should be affordable and easy to handle. The most common radiosynthetic route to [

18F]FDG is via the SN2 nucleophilic substitution of tetraacetyl mannose triflate, followed by C18 SPE immobilization, base hydrolysis, and elution. An alumina SPE cartridge is often included in series to remove chemical impurities such as [

18F]fluoride, tetrabutylammonium bicarbonate (TBAHCO3), or Kryptofix®. The synthesis of [

18F]
FDG for clinical use by common fully automated synthesizers requires over 30 min and achieves a radiochemical purity of over 95%. With the benchmarks established, we set out to test our open-source system [37].
Results and discussion

Development of the pump system
The flexible open-source microfluidic system we describe allows for the development of semi-automated flow processes. Parameters such as reaction conditions and flow rates were investigated and optimized. To fulfill the respective requirements, essential basic elements are needed. The most important task is to guarantee a continuous flow during the experiment. For this purpose, we built a syringe pump with two syringe holders that can be separately controlled. By using syringes as solvent reservoirs, a wide range of flow rates can be reliably covered.
Apart from the electronics and the mechanical parts, such as screws and rods, almost all components were 3D-printed. Figure 2 shows the CAD drawing and the assembled pump. We printed two versions of the pump, one in PLA (polylactic acid) and one in PETG (polyethylene terephthalate glycol copolymer), but also more chemical resistant materials like Nylon or any other non-flexible material should be possible.

Fig. 1 Synthesis of [ 18F]FDG


The 3D-printed parts were assembled using threaded inserts ensuring a firm fixation. The moving parts were guided by two rods and various ball and plain bearings. To transfer the motor movement to a linear movement, a trapezoidal thread spindle was used, which ensures a better power transmission than a standard V-threaded rod.
For controlling the pump, an Arduino Mega 2560 in combination with a programmable Nextion display was used. A RAMPS shield and TMC 2208 drivers were used to control the stepper motors. One drawback of using stepper motors is that pulsation of the flow can occur at low flow rates. This is caused when the pauses between steps are too long. For this reason, we chose geared stepper motors with a ratio of 27:1, resulting in two advantages. First, by increasing the number of steps required for one rotation, a constant flow could be ensured even at low flow rates. Second, the geared motor pump is much more powerful than the stepper motor and can easily generate pressures up to 10 bar, depending on the used syringes. One disadvantage is that the maximum pump speed is reduced. If needed, the gear motor can be easily changed to a smaller gear ratio, and the variable “gear-ratio” could be simply changed in the Arduino software (line 39: int gear-ratio=27). Of course, a smaller gear ratio leads not only to a faster pump speed but also a decrease in power and maximum pressure.
The system can be used with Hamilton glass syringes as well as commercially available disposable plastic syringes. To determine flow accuracy and reliability, the syringes were filled with water at r.t. and atmospheric pressure, the flow rate was set and the amount of collected water was weighed after equilibration of the system at the end of the collection time. Next, flow rates from 0.1 to 10% of the syringe volume were investigated. A modest deviation of 2.5%, which could not be decoupled from experimental error, was determined. From the data of the measurements, deviations for each examined flow rate can be created. If the deviation is over 2.5% the syringe/flowrate combination was deemed unsuitable for the pump. The results for the suggested flow rates are summarized in Table 1.
The measurements were carried out on both the PLA flow system and the PETG flow system. No significant differences were found. It was also investigated on both systems whether there were differences in the flow rate accuracy at higher pressure. For this purpose, all measurements of the Hamilton glass syringes were repeated at a pressure of 5 bar. Again, no significant differences were found. Detailed experimental data can be found in the ESI.

Development of the pressure sensor and BPR
Another important point is the continuous measurement of the pressure. Due to varying flow resistances at different flow rates, different viscosities of the running fluids, as well as lengths of the capillaries or other components used in the system, a unique basic pressure is established for the process. This pressure must be measured and displayed live so that real-time flow adjustments can be made. For this purpose, we have developed a pressure sensor (PS), which can communicate with the pump. The system was designed such that the designated maximum pressure will not be exceeded as the pump stops automatically, preventing the reactor from

Fig. 2 Exploded view CAD
drawing (a) and photograph (b) of the syringe pump
Table 1 | Suggested flow-range
for Hamilton-syringes | Syringe: Volume
[mL]

Suggested
flow-range
[μL/min]
0.1 | 1–10
0.25 | 1.25–25
1 | 5–100
2.5 | 2.5–250
5 | 5–500
10 | 10–1000
25 | 25–2500

bursting or another system component from rupturing. In addition, by tracking the pressure live, it is possible to know when the system is in equilibrium and ready to use.
The working principle of the pressure sensor is based on the resistance change of a force-sensitive resistor (FSR). To process the resistance change, the FSR is connected to an Arduino Mega on an analog Pin with enabled internal pullup resistor. The channel in the 3D-printed part is opened to form a cavity, allowing for the pressure of the system to be transmitted to the FSR. The cavity is sealed by a PTFE disc and damped by a silicone disc. We have used different materials and thicknesses for the discs and found that silicone with a thickness of 1 mm and PTFE with a thickness of 0.1 mm gives the best results for pressures between 0 and 6 bar.
As described in our previous publication [14], we found that a system with a guide rail gives reliably leakproof connections. The surfaces shown in Fig. 3 were sanded and the flangeless flat bottom 1/4″-28 fittings were pressed against the flat-honed surfaces.

Since each sensor is unique and has slight differences in measured pressure, it must be calibrated before use. The calibration can be done using a commercial manometer. Therefore, multiple data points from 0.5 to 6 bar were measured in 0.2 bar increments and converted to a calibration function. Detailed instructions for the calibration can be found in the ESI. The accuracy of our calibration was checked by multiple measurements of HPLC resistance cartridges. A maximum deviation of 0.7% at 6 bars could be determined. The kinetics of a reaction often correlate to temperature and reactant concentration. By increasing the pressure of the system, higher reaction temperatures (above the boiling point of the solvent) can be examined. For this purpose, we have designed an externally controllable back pressure regulator (BPR). In our previous publication [14] we developed a spring-based 3D-printed BPR. We have adapted the previous version to fit our guide rail (Fig. 3), which for us is the best and most reliable system. Also, we installed a 12 V gear motor to remotely tension and release the spring (Fig. 4). The motor is controlled using an L298N motor driver,


Fig. 3 Exploded view CAD
drawing (a) and photograph (b) of the pressure sensor


Fig. 4 Exploded view CAD
drawings and photographs of the motorized BPR (a, b), the manual BPR (c), and the control unit (d)

which is connected to the Arduino Mega from the sensor. This remote control makes it possible to set the desired pressure when the setup is not easily accessible during the experiment. An example of this is when the components are placed in a shielded lead hotcell during experiments with high amounts of radioactivity. For our applications (PS and BPR), the solvent touching parts were 3D-printed with PEEK (polyether ether ketone), due to its high chemical and temperature resistance, but we also evaluated PP, PVDF, and PETG. All parts are working equally well with all tested materials, so a suitable material for each application can be selected. With the selected components, pressures up to 10 bar could be reliably reached.

Radiofluorination
Radiochemical syntheses are generally performed behind shielding as this reduces the radiation dose and contributes to safer working. Thus, non-direct intervention in the synthesis to control or vary the reaction parameters is a major benefit to the chemist.
To determine whether the system meets the high requirements of an established synthesis, a semi-automated process for the preparation of [

18F]2-fluoro-2-desoxy-d-glucose ([¹⁸F]FDG) was developed and compared to the conventional batch process. Therefore, the synthesis was investigated under the same reaction conditions for both methods. For quantification, the radio-TLC measurement and HPLC measurements are used to determine the corrected radiochemical yield (RCY) and the radiochemical purity (RCP).
[

18F]HF was obtained as an aqueous solution from the cyclotron, concentrated using a preconditioned ion exchange SPE, and eluted with a solution of MeCN and TBA bicarbonate. The reaction solution was azeotropically dried with anhydrous MeCN at 100 °C under an argon stream. After several drying cycles, the dry [

18F]fluoride was dissolved in 1 mL of anhydrous MeCN. This reaction solution serves as the fluorinating agent.
For the batch synthesis, aliquots of 100 µL of the azeotropically dried [

18F]fluoride were added to 60 µL of the acetylated mannose triflate solution into a disposable Pyrex tube and quickly vortexed. The radiofluorination reactions were carried out at 80, 90, 110, and 110 °C. The reaction time was set to 5, 10, and 15 min. The quality of the fluorination of each condition was quantified via radio-TLC and HPLC. After cooling to around 50 °C, the reaction mixtures were diluted with water. The diluted solution was then pushed through a SEP-Pak Alumina N SPE cartridge, connected in series to a C18 SPE cartridge.
The flow synthesis system of [

18F]FDG consists of our
syringe pump, a 6-way valve with a built-in PEEK loop (160 µL), our pressure sensor, the remotely controllable pressure regulator, two 3D-printed PEEK reactors (900 µL and 50 µL) and two cartridges (SEP-Pak Alumina N (Waters) and Sep-Pak Plus Light C18 cartridge) (Fig. 5). Acetonitrile is used as a solvent and is continuously delivered to the system from a 10 mL syringe by the syringe pump. All components are connected using ETFE capillaries with an inner diameter of 0.5 mm and flangeless flat bottom 1/4″-28 HPLC fittings. The use of a 6-way valve allows pressure to be applied to the system at continuous flow. Reactions can thus be carried out at temperatures above the boiling point of the solvent under continuous flow. The pressure sensor is connected between the 6-way valve and the pump to avoid unnecessary radioactive contamination and unnecessary dead volume. Aliquots of 100 µL of the [

18F]fluoride in MeCN were
premixed with 60 µL of the acetylated mannose triflate in dry MeCN. The pressure of the system was set to 2.5 bar. The reaction mixture was injected onto the loop of the 6-way valve, and into the running process by switching the 6-way valve. By changing the flow rate of the solvent, the residence or reaction time can be directly determined. Reaction times of 5, 10, and 15 min at 80, 90, 100, and 110 °C were investigated. Every condition was quantified via radio-TLC and HPLC. The results are summarized in Table 2. Temperatures above 100 °C appear to destroy the precursor, and at temperatures below 90 °C the conversion is significantly lower. While a clear trend can be seen in the reaction times, one must also consider the half-life of the isotope of choice. Although a slightly better conversion is obtained with a residence time of 15 min, it is negligible. Under batch as well as under flow conditions, the optimum temperature was found to be 90 °C with a residence time of 10 min. To be able to make a statistical statement, repetitions of these conditions were carried out. For the batch synthesis, an RCY value of 52.3% ± 1.9% (n=4) could be determined. For the flow system, an RCY value of 47.6% ± 1.2% (n=5) could be determined (Table 3). Both radiochemical yields are in a similar range.
It is noticeable that considerably fewer radioactive by-products are produced under flow conditions (Fig. 6). This is a notable advantage of our flow synthesis for tracers with no included HPLC purification step such as [

18F]FDG.
Another advantage of the flow system is that purification and deprotection can be automatically integrated into the process. For this purpose, the reaction solution is diluted 9-fold with water and passed through a Sep-Pak alumina cartridge, which is used to remove unwanted polar impurities such as [

18F]fluoride. The acetylated intermediate can then be trapped on a C18 SPE cartridge that is connected afterward in series. Tests have shown that a dilution of 10% MeCN to 90% H2O is necessary. Even with 15% MeCN to 85% H2O, the fully acetylated intermediate is no longer reliably immobilized on the C18 cartridge. To verify the

18F]FDG.

quality of the purification, the acetylated [

18F]FDG was
eluted from the C18 SPE cartridge with ethanol and examined by radio-TLC and HPLC. A radiochemical purity (RCP) of 99.1% ± 0.7% (n=5) was observed. In comparison, the purification of the batch synthesis was performed manually. In this case, a purity of 93.5% ± 1.4% (n=4) was determined. As expected, the purification of flow synthesis is simpler and more efficient than the manual batch process due to fewer by-products. Considering only small differences in RCY, this is an immense gain for radiochemical applications.
Deprotection was, in both cases, manually performed directly on the cartridge by passing 0.5 mL of 2 M NaOH through the C18 SPE cartridge. We performed a subsequent neutralization and formulation with 0.25 mL of 6 M HCl, followed by 1 mL of 1 M NaHCO3. The deprotected [

18F]FDG
was quantified via radioactive TLC.
The total time required for the semiautomated radiofluorination and immobilization of the acetylated intermediate on the C18 SPE cartridge was 14 min. The manual deprotection with aqueous NaOH required an additional minute. Thus, [

18F]
FDG was produced in under 15 min and had, according to radio-TLC, a radiochemical purity above 99%.
Fig. 5 | Schematic drawing of the flow process for [
Table 2 | Results fluorination
Temperature [°C] | Residence time [min] | RCY Batch [%] | RCY Flow [%]
| 5 | 27.1 | 25.2
80 | 10 | 31.2 | 29.2
| 15 | 33.8 | 30.1
| 5 | 45.9 | 37.2
90 | 10 | 54.9 | 47.2
| 15 | 55.8 | 48.1
| 5 | 38.2 | 28.1
100 | 10 | 45.6 | 38.4
| 15 | 47.9 | 39.1
| 5 | 22.5 | 15.2
110 | 10 | 20.2 | 13.2
| 15 | 16.5 | 9.2
Table 3 | Labelling at 90 °C/10 min
Number # | RCY Batch [%] | RCY Flow [%]
1 | 49.2 | 47.2
2 | 54.9 | 45.2
3 | 53.7 | 46.1
4 | 51.5 | 48.2
5 | | 51.2
| 52.3% ± 1.9% (n=4) | 47.6% ± 1.2% (n=5)


Experimental

Chemical reactions
If not mentioned, all reagents and solvents were purchased from commercial suppliers and used without further purification. The precursor, mannose triflate ultra-pure was purchased from ABX, Germany.

General radiochemistry
The [

18F]fluoride was produced on a medical cyclotron (PETtrace 800, GE Healthcare) using the nuclear reaction of ¹⁸O(p,n)¹⁸F. Content of free [

18F]fluoride
as well as reaction products were analyzed by thin layer chromatography (TLC, PolyGram Sil G/UV254, Macherey–Nagel, Dueren, Germany) and analyzed on a Cyclone Plus phosphorimager (Perkin Elmer, Waltham, Massachusetts, USA). Radio-HPLC was performed using an Agilent 1260 series system (Agilent, Santa Clara, USA), with a reverse-phase analytical column (Luna C18(2), 100 Å, 250 × 4.6 mm, 5 μm; Phenomenex, Torrance, California, USA) connected to a Flow Count detection system (Model 106, Eckert & Ziegler, Berlin, Germany ) coupled to a diode detector (B-FC-3500-A, Eckert & Ziegler, Berlin, Germany). The mobile phases comprised CH3CN and water (+ 0.1% TFA) and the flow rate was 1 mL/min. The standard gradient program started with 5% CH3CN for 2 min. The CH3CN component was then increased to 100% over 15 min, where it was maintained for a further 6 min.

General procedure for fluoride preparation
Sep-Pak Plus Light QMA Carb (Waters, Waltham, MA, USA) was preconditioned with 10 mL 1 M NaHCO3, 10 mL air, 10 mL H2O, and 10 mL air. Sep-Pak Plus Light C18 SPE cartridge (Waters) was preconditioned with 10 mL ethanol and 10 mL H2O. SEP-Pak Alumina N (Waters) was preconditioned with 5 mL MeCN.
[

18F]fluoride was immobilized on the QMA cartridge and eluted into a glass reactor with 0.6 mL of a premixed solution containing TBA-HCO3 (300 µL, 0.075 M, ABX, Germany) diluted with 0.3 mL dry MeCN. Azeotropical drying was carried out at 100 °C under a flow of argon and aided by multiple additions of MeCN (4×1 mL).

General procedure for the flow‑synthesis of [

18F]FDG
[38, 39]
Aliquots (100 µL) of the azeotropically dried [

18F]fluoride
were dissolved in MeCN. 60 µL of mannose triflate solution (3 mg, 0.3 mL dry MeCN) was added to the 100 µL [

18F]
fluoride aliquot and quickly vortexed. The pressure of the setup was set to 2.5 bar. In a continuous flow, the premixed reaction mixture was injected through a 6-way valve into the running process. The radiofluorination was carried out at 80, 90, 110, and 110 °C. The flow rates were adjusted so that reaction times of 5, 10, and 15 min could be investigated (calculation of flow rates: Table 4). To determine the quality of the radio-fluorination, the acetylated intermediate was qualified via radio-TLC (petroleum ether/ ethyl acetate 50:50) and HPLC (tr = 14.34 min) before the deprotection took place. The process was repeated at reaction temperatures of 80, 90, 100, and 110 °C, and the optimal conditions were ascertained. To continue the process, a second syringe delivering water facilitated the dilution in the second 50 µL PEEK reactor. The diluted mixture passed through a SEP-Pak Alumina N (Waters) SPE cartridge connected in series to a Sep-Pak Plus Light C18 SPE cartridge, resulting in the immobilization of the acetylated intermediate on the latter. The deprotection was performed manually with 0.5 mL 2 M
Fig. 6 | Radio TLC batch vs. flow after ¹⁸F-labelling
Table 4 | Calculated flow rates
Reaction time
[min] | Fluorination flow rate [μL/min]

Dilution with
water flow
rate [μL/min]

Retention
time dilution
with water
[min]

Water
content
5 | 180
| 180

1620
1530

0.03
0.03

90%
85%
10 | 90
| 90

810
765

0.06
0.06

90%
85%
15 | 60
| 60

540
510

0.08
0.09

90%
85%

NaOH. The solution was neutralized with 0.25 mL 6 M HCl and buffered with 1 mL sat. NaHCO3 afterward. The deprotected [

18F]FDG was qualified via HPLC (tr = 2.88 min) and radioactive TLC (MeCN/H2O 95:5).
Acetylated [18F]FDG intermediate RCY: 47.6% ± 1.2% (n = 5)Radiochemical purities of[18F]FDG (RCPs): 99.1% ± 0.7% (n = 5)

General procedure for the batch‑synthesis of [

18F]
FDG
The fluoride and aliquot preparation were performed as described above. The radiofluorination reactions were performed in disposable Pyrex 7 mL tubes and were carried out at 80, 90, 110, and 110 °C. The reaction time was set to 5, 10, and 15 min. After cooling to around 50 °C, the reaction mixtures were diluted with 2 mL H2O. The diluted solution was then pushed through a SEP-Pak Alumina N SPE (Waters), connected in series to a C18 SPE cartridge. Either the acetylated intermediate was eluted with ethanol (0.5 mL) or deprotection was carried out as described above. The radiochemical yield of the acetylated intermediate was measured by radio-TLC (petroleum ether/ ethyl acetate 50:50) before the purification by alumina SPE. Purity was determined afterward. The deprotection was performed by passing 0.5 mL 2 M NaOH directly through the Sep-Pak Plus Light C18 cartridge (Waters) containing the acetylated derivative. The solution was neutralized with 0.25 mL 6 M HCl and buffered with 1 mL sat. NaHCO3 afterward. The products were qualitatively assessed as described above. Acetylated [18F]FDG intermediate RCY: 52.3% ± 1.9% (n = 4)Radiochemical purities of[18F]FDG (RCPs): 93.5% ± 1.4% (n = 4)

Conclusion

In this work, we have developed a 3D-printed open-source microfluidic system that includes a dual syringe pump, a pressure sensor, and a remotely controlled back pressure regulator, all of which can be built for around 500 €. Owing to its high customizability, this low-cost open-source microfluidic system shows great potential in all fields of chemical research. Especially, due to its small footprint, the ever-expanding world of radiochemistry could benefit significantly. Using the [

18F]FDG radiosynthesis as a benchmark, we confirmed that our system can reliably perform the functions and operations that are carried out by proprietary and expensive radiosynthesizers e.g. radiofluorination, dilution, and SPE purification. The system was thoroughly evaluated and shown to be suitable for research radiochemistry, producing results that are comparable to common batch syntheses. It can be used to synthesize radiotracers in good yield with fewer radioactive side-products compared to batch syntheses. The system is easily expandable and can be adapted to include multiple reactors and SPE purification steps, all while maintaining a footprint small enough to fit in a hotcell. The potential for this system is immense for both manual and automated radiochemistry. The automation of manual steps would reduce the overall radiation exposure to the laboratory staff while increasing reliability and reproducibility by eliminating human error. The system could also be coupled to existing radiosynthesizers, producing radioactive prosthetic ligands for more complicated, multistep radiosynthesis.
With the presented plans, descriptions, and schematics of this open-source flow system we aim to inspire other scientists to use this technology and ultimately remove some of the barriers surrounding the fascinating fields of flow- and radiochemistry.
ESM 1 3D printer setup, numbered part lists, detailed step-bystep assembly instructions end electronic setups of all components. (PDF 1.94 MB)Supplementary information The online version contains supplementary material available at https://doi.org/10.1007/s41981-023-00267-z. (https://doi.org/10.1007/s41981-023-00267-z)
Acknowledgements We thank the Karl und Anna Buck Stiftung for funding this work.
Funding Open Access funding enabled and organized by Projekt DEAL.
Declarations
Conflict of interest On behalf of all authors, the corresponding author states that there is no conflict of interest.
Open Access This article is licensed under a Creative Commons Attribution 4.0 International License, which permits use, sharing, adaptation, distribution and reproduction in any medium or format, as long as you give appropriate credit to the original author(s) and the source, provide a link to the Creative Commons licence, and indicate if changes were made. The images or other third party material in this article are included in the article's Creative Commons licence, unless indicated otherwise in a credit line to the material. If material is not included in the article's Creative Commons licence and your intended use is not permitted by statutory regulation or exceeds the permitted use, you will need to obtain permission directly from the copyright holder. To view a copy of this licence, visit http://creativecommons.org/licenses/by/4.0/.

References

1. Plutschack MB, Pieber B, Gilmore K, Seeberger PH (2017) The Hitchhiker’s guide to flow chemistry. Chem Rev 117:11796– 11893. https://doi.org/10.1021/acs.chemrev.7b00183
2. Gutmann B, Kappe CO (2017) Forbidden chemistries — paths to a sustainable future engaging continuous processing. J Flow Chem 7:65–71. https://doi.org/10.1556/1846.2017.00009
3. Hughes DL (2020) Applications of flow chemistry in the pharmaceutical industry—Highlights of the recent patent literature.

Org. Process Res Dev 24:1850–1860. https://doi.org/10.1021/acs.oprd.0c00156 (https://doi.org/10.1021/acs.oprd.0c00156)
4. Bogdan AR, Dombrowski AW (2019) Emerging trends in flow chemistry and applications to the pharmaceutical industry. J Med Chem 62:6422–6468. https://doi.org/10.1021/acs.jmedc hem.8b01760 (https://doi.org/10.1021/acs.jmedchem.8b01760)
5. Wegner J, Ceylan S, Kirschning A (2011) Ten key issues in modern flow chemistry. Chem Commun 47:4583–4592. https://doi.org/10.1039/C0CC05060A
6. Zhang J, Wang K, Teixeira AR, Jensen KF, Luo G (2017) Design and scaling up of microchemical systems: a review. Annu Rev Chem Biomol Eng 8:285–305. https://doi.org/10.1146/annurev-chembioeng-060816-101443 (https://doi.org/10.1146/annurev-chembioeng-060816-101443)
7. Berton M, de Souza JM, Abdiaj I, McQuade DT, Snead DR (2020) Scaling continuous API synthesis from milligram to kilogram: extending the enabling benefits of micro to the plant. J Flow Chem 10:73–92. https://doi.org/10.1007/s41981-019-00060-x (https://doi.org/10.1007/s41981-019-00060-x)
8. Dong Z, Wen Z, Zhao F, Kuhn S, Noël T (2021) Scale-up of micro- and milli-reactors: an overview of strategies, design principles and applications. Chem Eng Sci : X 10:100097. https://doi.org/10.1016/j.cesx.2021.100097
9. Buglioni L, Raymenants F, Slattery A, Zondag SDA, Noël T (2022) Technological innovations in photochemistry for organic synthesis: Flow chemistry, high-throughput experimentation, scale-up, and photoelectrochemistry. Chem Rev 122:2752–2906. https://doi.org/10.1021/acs.chemrev.1c00332
10. Tanimu A, Jaenicke S, Alhooshani K (2017) Heterogeneous catalysis in continuous flow microreactors: a review of methods and applications. Chem Eng J 327:792–821. https://doi.org/10.1016/j.cej.2017.06.161 (https://doi.org/10.1016/j.cej.2017.06.161)
11. Pletcher D, Green RA, Brown RCD (2018) Flow electrolysis cells for the synthetic organic chemistry laboratory. Chem Rev 118:4573–4591. https://doi.org/10.1021/acs.chemrev. 7b00360 (https://doi.org/10.1021/acs.chemrev.7b00360)
12. Price AJN, Capel AJ, Lee RJ, Pradel P, Christie SDR (2020) An open source toolkit for 3D printed fluidics. J Flow Chem. https://doi.org/10.1007/s41981-020-00117-2
13. Neumaier JM, Madani A, Klein T, Ziegler T (2019) Lowbudget 3D-printed equipment for continuous flow reactions. Beilstein J Org Chem 15:558–566. https://doi.org/10.3762/bjoc.15.50 (https://doi.org/10.3762/bjoc.15.50)
14. Menzel F, Klein T, Ziegler T, Neumaier JM (2020) 3D-printed PEEK reactors and development of a complete continuous flow system for chemical synthesis. React Chem Eng 5:1300–1310. https://doi.org/10.1039/D0RE00206B
15. Parra-Cabrera C, Achille C, Kuhn S, Ameloot R (2018) 3D printing in chemical engineering and catalytic technology: structured catalysts, mixers and reactors. Chem Soc Rev 47:209–230. https://doi.org/10.1039/C7CS00631D
16. Alimi OA, Meijboom R (2021) Current and future trends of additive manufacturing for chemistry applications: a review. J Mater Sci 56:16824–16850. https://doi.org/10.1007/s10853-021-06362-7 (https://doi.org/10.1007/s10853-021-06362-7)
17. Capel AJ, Rimington RP, Lewis MP, Christie SDR (2018) 3D printing for chemical, pharmaceutical and biological applications. Nat Rev Chem 2:422–436. https://doi.org/10.1038/s41570-018-0058-y (https://doi.org/10.1038/s41570-018-0058-y)
18. Baas S, Saggiomo V (2021) Ender3 3D printer kit transformed into open, programmable syringe pump set. HardwareX 10:e00219. https://doi.org/10.1016/j.ohx.2021.e00219
19. Wijnen B, Hunt EJ, Anzalone GC, Pearce JM (2014) Open-source syringe pump library. PLoS ONE 9:e107216. https://doi.org/10.1371/journal.pone.0107216
20. Saggiomo V (2022) A 3D printer in the lab: not only a Toy. Adv Sci 9:2202610. https://doi.org/10.1002/advs.202202610
21. Steel CJ, O’Brien AT, Luthra SK, Brady F (2007) Automated PET radiosyntheses using microfluidic devices. J Label Compd Radiopharm 50:308–311. https://doi.org/10.1002/jlcr.1259
22. Koag MC, Kim H-K, Kim AS (2014) Efficient microscale synthesis of [¹⁸F]-2-fluoro-2-deoxy-d-glucose. Chem Eng J 258:62–68. https://doi.org/10.1016/j.cej.2014.07.077
23. Watts P, Pascali G, Salvadori PA (2012) Positron emission tomography radiosynthesis in microreactors. J Flow Chem 2:37–42. https://doi.org/10.1556/jfc-d-12-00010
24. Culbert PA, Adam MJ, Hurtado ET, Huser JMA, Jivan S, Lu J, Ruth TJ, Zeisler SK (1995) Automated synthesis of [

18F]
FDG using tetrabutylammonium bicarbonate. Appl Radiat Isot 46:887–891. https://doi.org/10.1016/0969-8043(95)00177-F
25. Vander Heiden MG, Cantley LC, Thompson CB (2009) Understanding the Warburg effect: the metabolic requirements of cell proliferation. Science 324:1029–1033. https://doi.org/10.1126/science.1160809 (https://doi.org/10.1126/science.1160809)
26. Palsson-McDermott EM, O’Neill LA (2013) The Warburg effect then and now: from cancer to inflammatory diseases. BioEssays 35:965–973. https://doi.org/10.1002/bies.20130 0084 (https://doi.org/10.1002/bies.201300084)
27. Robey IF, Stephen RM, Brown KS, Baggett BK, Gatenby RA, Gillies RJ (2008) Regulation of the Warburg effect in earlypassage breast cancer cells. Neoplasia 10:745–756. https://doi.org/10.1593/neo.07724 (https://doi.org/10.1593/neo.07724)
28. Glaudemans AW, Signore A (2010) FDG-PET/CT in infections: the imaging method of choice? Eur. J Nucl Med Mol Imaging 37:1986–1991. https://doi.org/10.1007/s00259-010-1587-x
29. Gafter-Gvili A, Raibman S, Grossman A, Avni T, Paul M, Leibovici L, Tadmor B, Groshar D, Bernstine H (2015) [

18F]FDG-PET/CT for the diagnosis of patients with fever of unknown origin. QJM 108:289–298. https://doi.org/10.1093/qjmed/hcu193 (https://doi.org/10.1093/qjmed/hcu193)
30. Wang ZG, Yu MM, Han Y, Wu FY, Yang GJ, Li DC, Liu SM (2016) Correlation of Glut-1 and Glut-3 expression with F-18 FDG uptake in pulmonary inflammatory lesions. Med (Baltim) 95:e5462. https://doi.org/10.1097/md.0000000000005462
31. Yu S (2006) Review of F-FDG synthesis and quality control. Biomed Imaging Interv J 2:e57. https://doi.org/10.2349/biij.2. 4.e57 (https://doi.org/10.2349/biij.2.4.e57)
32. Turkington TG (2001) Introduction to PET instrumentation. J Nucl Med Technol 29:4–11. https://tech.snmjournals.org/content/29/1/4 (https://tech.snmjournals.org/content/29/1/4)
33. Melcher CL (2000) Scintillation crystals for PET. J Nucl Med 41:1051–1055. https://jnm.snmjournals.org/content/41/6/1051
34. Oh SJ, Chi DY, Mosdzianowski C, Kim JY, Gil HS, Kang SH, Ryu JS, Moon DH (2005) Fully automated synthesis of [18F] fluoromisonidazole using a conventional [18F]FDG module. Nucl Med Biol 32:899–905. https://doi.org/10.1016/j.nucme dbio.2005.06.003 (https://doi.org/10.1016/j.nucmedbio.2005.06.003)
35. Decristoforo C (2007) Challenges in the small-scale preparation of radiopharmaceuticals -A European perspective. FABAD J Pharm Sci 32:131–138. http://dergi.fabad.org.tr/index/issue/abstract/32_03_5.htm (http://dergi.fabad.org.tr/index/issue/abstract/32_03_5.htm)
36. Unterweger MP, Fitzgerald R (2020) Corrigendum to “Update of NIST half-life results corrected for ionization chamber sourceholder instability” [Appl. Radiat. Isot. 87 (2014) 92–94]. Appl Radiat Isot 159:108976. https://doi.org/10.1016/j.apradiso.2019. 108976 (https://doi.org/10.1016/j.apradiso.2019.108976)
37. Saxena P, Singh AK, Dixit M, Kheruka SC, Mahmood T, Gambhir S (2021) Establishing the [18F]-FDG production via two different automated synthesizers for routine clinical studies: our institutional experiences of 4 years. Indian J Nucl Med 36:120–
124. https://doi.org/10.4103/ijnm.IJNM_137_20
38. Gomzina NA, Zaitsev VV, Krasikova RN (2001) Optimization of nucleophilic fluorination step in the synthesis of various compounds labelled with fluorine-18 for their use as pet radiotracers. J Label Compd Radiopharm 44:S895–S897. https://doi.org/10.1002/jlcr.25804401314 (https://doi.org/10.1002/jlcr.25804401314)
39. Zhou X, Li Y, Jiang X, Wang X, Chen S, Shen T, You J, Lu H, Liao H, Li Z, Cheng Z (2020) Intra-individual comparison of 18F-PSMA-1007 and 18F-FDG PET/CT in the evaluation of patients with prostate cancer. Front Oncol 10:585213. https://doi.org/10.3389/fonc.2020.585213 (https://doi.org/10.3389/fonc.2020.585213)
Publisher’s note Springer Nature remains neutral with regard to jurisdictional claims in published maps and institutional affiliations.

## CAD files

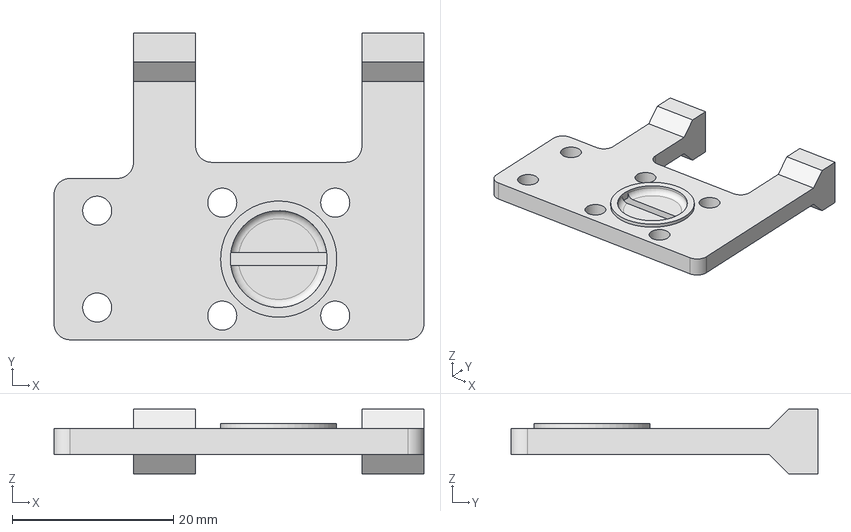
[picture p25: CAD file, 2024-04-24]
CAD files/40 - pressure sensor main body.stp
45.9 x 38.0 x 8.00 mm

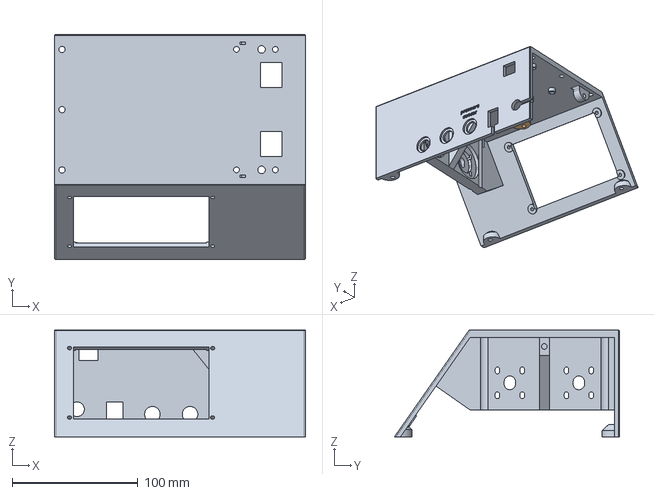
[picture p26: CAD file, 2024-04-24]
CAD files/01 - main pump body.stp
200.0 x 179.5 x 85.0 mm

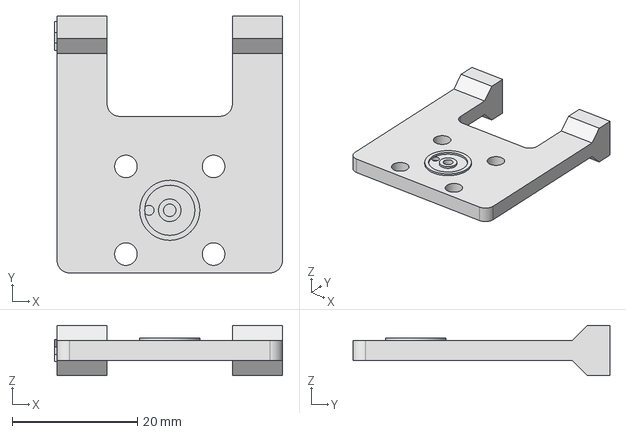
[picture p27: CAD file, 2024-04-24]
CAD files/56 - BPR main body.stp
36.4 x 41.0 x 8.00 mm

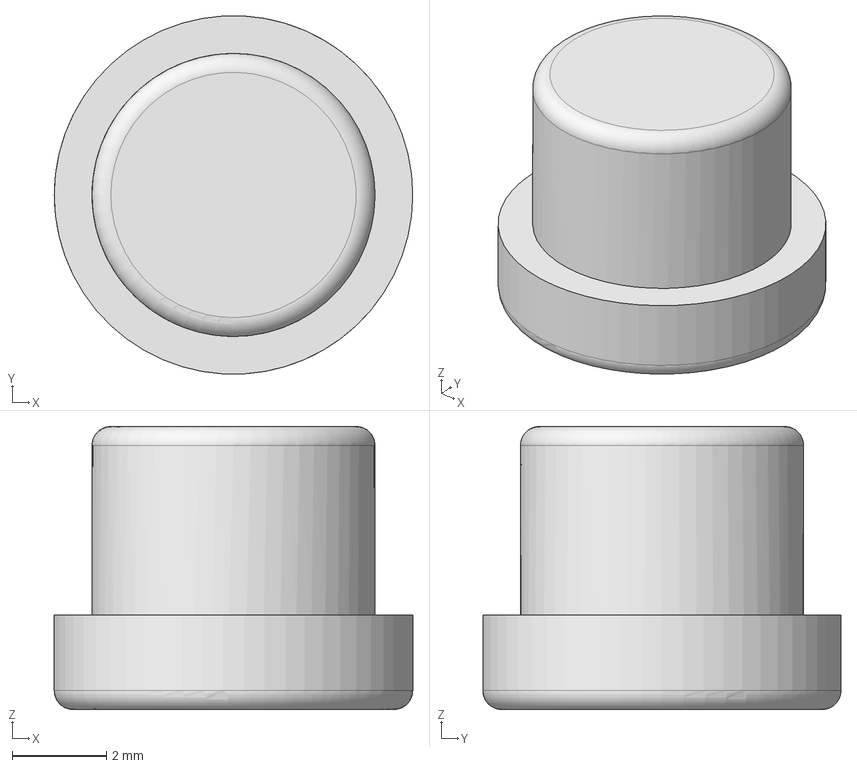
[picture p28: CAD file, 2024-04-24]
CAD files/61 - spring cap.stp
7.60 x 7.59 x 6.00 mm

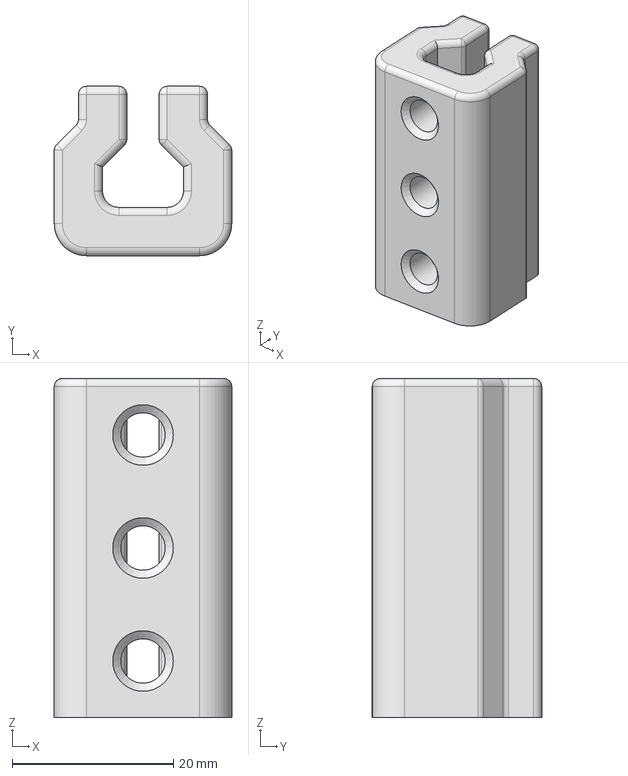
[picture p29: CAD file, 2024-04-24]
CAD files/41 - guide rail - 3 inlets.stp
22.0 x 21.0 x 42.0 mm

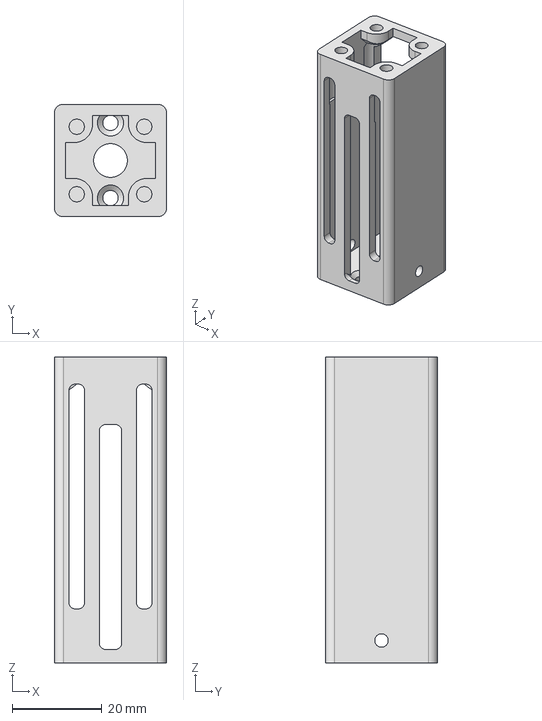
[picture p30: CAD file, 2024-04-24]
CAD files/58 - motor mount.stp
25.0 x 25.0 x 68.0 mm

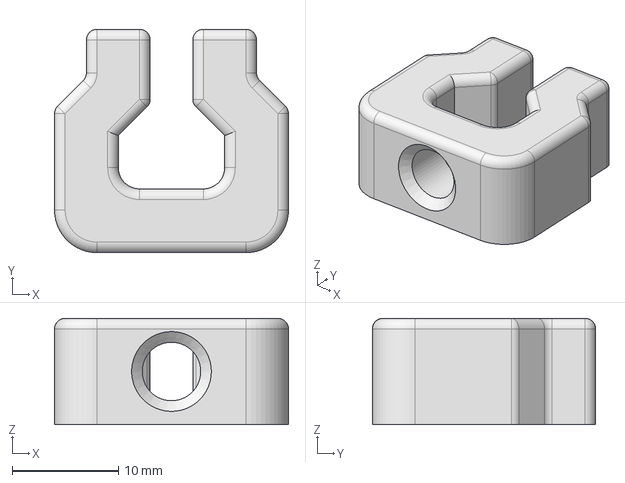
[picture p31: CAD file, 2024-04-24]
CAD files/41 - guide rail - 1 inlet.stp
22.0 x 21.0 x 10.0 mm

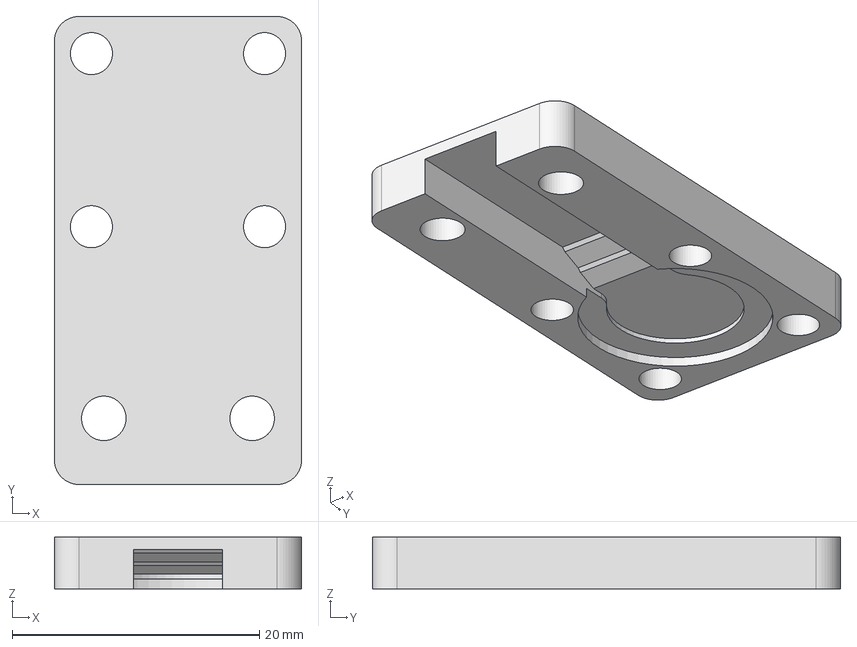
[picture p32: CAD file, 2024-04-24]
CAD files/42 - Pressure sensor lid.stp
20.0 x 37.9 x 4.20 mm

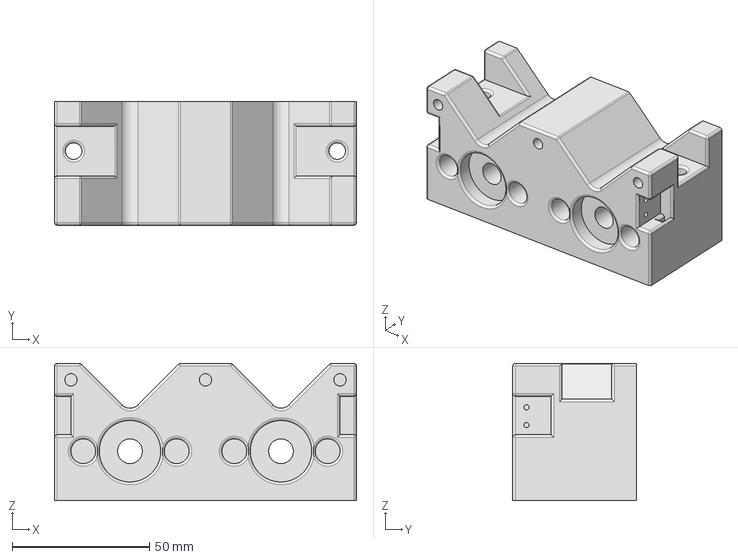
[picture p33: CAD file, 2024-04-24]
CAD files/03 - syringe holder block.stp
110.0 x 45.0 x 50.0 mm

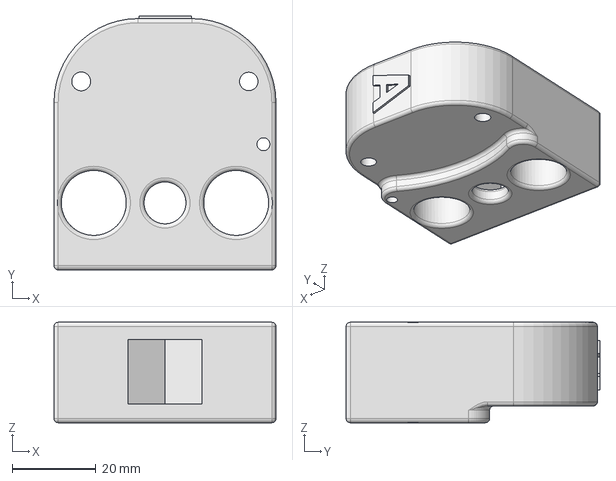
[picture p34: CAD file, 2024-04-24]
CAD files/06 - carrier block A.stp
53.0 x 60.6 x 24.0 mm

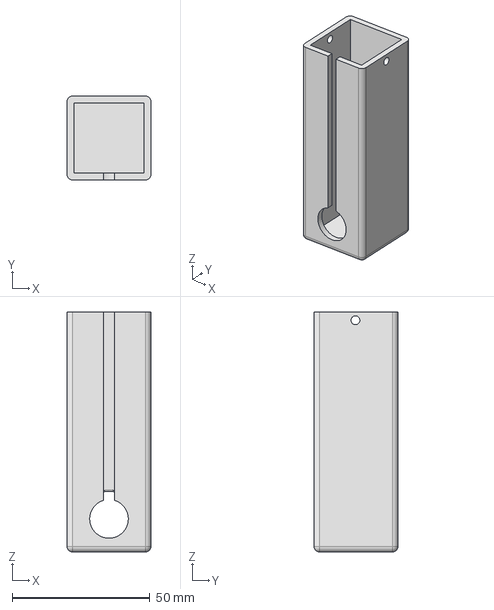
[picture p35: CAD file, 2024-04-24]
CAD files/60 - motor cover.stp
30.4 x 30.4 x 87.0 mm

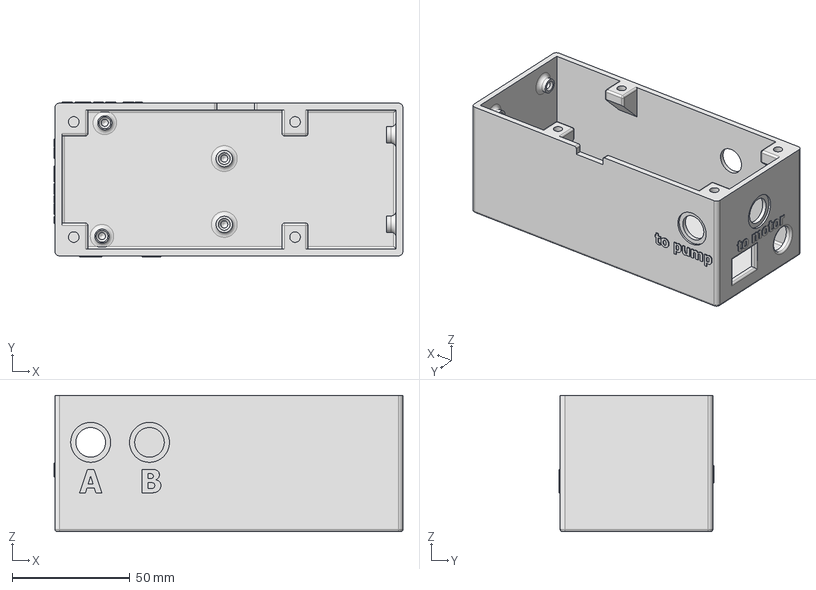
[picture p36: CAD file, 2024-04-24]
CAD files/46 - electronic case.stp
148.4 x 65.8 x 58.0 mm

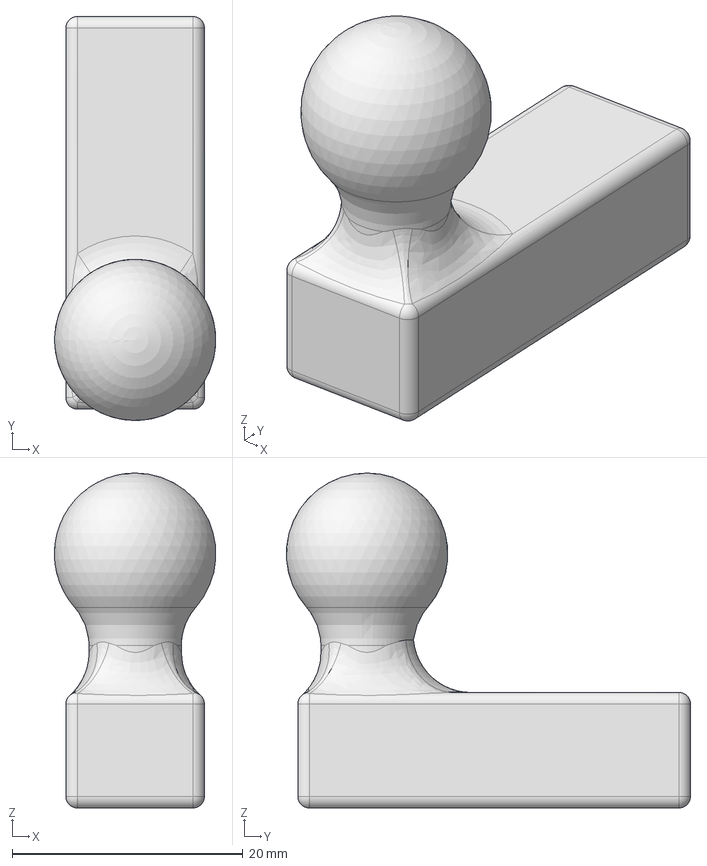
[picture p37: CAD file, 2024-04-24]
CAD files/08 - syringe clamp.stp
14.0 x 35.0 x 29.0 mm

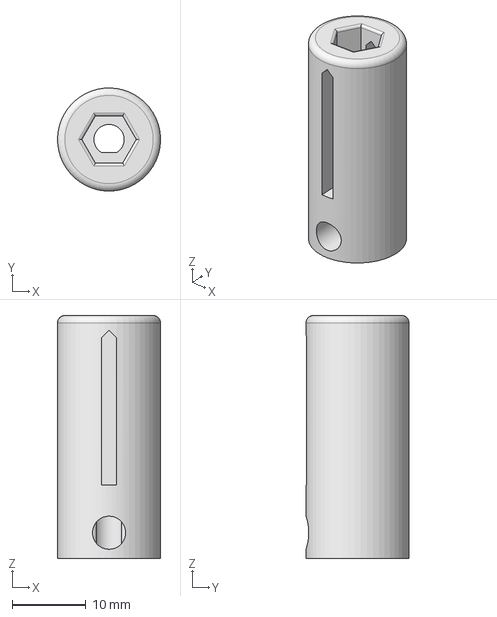
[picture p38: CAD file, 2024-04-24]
CAD files/59 - motor shaft coupler.stp
14.0 x 14.0 x 33.0 mm

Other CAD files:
CAD files/05 - End plate.stp
CAD files/11 - syringe retainer front.stp
CAD files/09 - display frame.stp
CAD files/54 - pressure gauge holder.stp
CAD files/01 - main pump body.stl
CAD files/02 - bottom part.stl
CAD files/02 - bottom part.stp
CAD files/03 - syringe holder block.stl
CAD files/04 - Front plate.stl
CAD files/04 - Front plate.stp
CAD files/05 - End plate.stl
CAD files/06 - carrier block A.stl
CAD files/07 - carrier block B.stl
CAD files/07 - carrier block B.stp
CAD files/08 - syringe clamp.stl
CAD files/09 - display frame.stl
CAD files/10 - syringe retainer back.stl
CAD files/10 - syringe retainer back.stp
CAD files/11 - syringe retainer front.stl
CAD files/40 - pressure sensor main body.stl
CAD files/41 - guide rail - 1 inlet.stl
CAD files/41 - guide rail - 2 inlets.stl
CAD files/41 - guide rail - 2 inlets.stp
CAD files/41 - guide rail - 3 inlets.stl
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

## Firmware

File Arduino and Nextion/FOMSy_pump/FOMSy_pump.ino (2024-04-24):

#include <Nextion.h>          // Nextion Library by Bentley Born https://github.com/bborncr/nextion
#include <SoftwareSerial.h>   // Software Serial Port (included in Arduino IDE "no download")
SoftwareSerial nextion(50, 51);// Nextion TX connected to Arduino pin 50 and RX to pin 51

Nextion myNextion(nextion, 9600); // Setup of Nextion library with name NextionLCD at 9600bps

// X Motor on shield, define pins / motor syringe A
#define stepa A0
#define dira A1
#define enablea 38
#define stopa 2   //X+ on  Shield

// Y Motor on  shield, define pins / motor syringe B
#define stepb A6
#define dirb A7
#define enableb A2
#define stopb 3

// signal in from pressure sensor
#define presstooa A11
#define presstoob A12

long delaya = 240384;
long delayb = 240384;
long flowa = 5;
long flowb = 5;
byte flowdeza = 0;
byte flowdezb = 0;
unsigned long flowfina = 0;
unsigned long flowfinb = 0;
byte diaa = 0;
byte diab = 0;
byte diadeza = 0;
byte diadezb = 0;
unsigned long radfina = 0; //final radius * 1000
unsigned long radfinb = 0; //final radius * 1000
unsigned long syringefactora = 12732;  //syringefactor in µm/mL
unsigned long syringefactorb = 12732;  //syringefactor in µm/mL
unsigned long gearratio = 27;
unsigned long microsteps = 4;
unsigned long factor = 450000000; // factor from mm/mL --> µL/min for 1:1 ratio and microsteps = 1 (no microsteps)  (60*1000*1000 [µs] / (200 [steps per round  / 1,5 [mm per round, thread pitch] /1000)) =  450000000
unsigned long previousMicrosa = 0;
unsigned long previousMicrosb = 0;
unsigned long preva = 0;
unsigned long prevb = 0;
unsigned long addeda = 0;
unsigned long addedb = 0;
unsigned long pressuretimea = 0;
unsigned long pressuretimeb = 0;
unsigned long addedfina = 0;
unsigned long addedfinb = 0;

byte statea = 0;
byte stateb = 0;
byte timestatea = 0;
byte timestateb = 0;
byte toohigha = 0;
byte toohighb = 0;
byte pulla = 0;
byte pullb = 0;
byte pusha = 0;
byte pushb = 0;
unsigned long stepsa = 0;
unsigned long stepsb = 0;
unsigned long i = 0;
unsigned long j = 0;
unsigned long k = 0;
unsigned long l = 0;

String message;   // received message for Nextion LCD

void setup()
{
  // define pins
  pinMode(stepa, OUTPUT);
  pinMode(dira, OUTPUT);
  pinMode(enablea, OUTPUT);
  digitalWrite(enablea, HIGH);     //LOW = enable
  pinMode(stopa, INPUT);
  digitalWrite(stopa, HIGH); // turn on pullup resistors

  pinMode(stepb, OUTPUT);
  pinMode(dirb, OUTPUT);
  pinMode(enableb, OUTPUT);
  digitalWrite(enableb, HIGH);
  pinMode(stopb, INPUT);
  digitalWrite(stopb, HIGH); // turn on pullup resistors

  pinMode(presstooa, INPUT);
  digitalWrite(presstooa, HIGH); // turn on pullup resistors
  pinMode(presstoob, INPUT);
  digitalWrite(presstoob, HIGH); // turn on pullup resistors
  myNextion.init();

  factor = 450000000 / microsteps / gearratio; // calculate the factor with microsteps and gearratio

}
void loop() {

  //------------------------------------------------------------------------------------------
  //  buttons action
  //------------------------------------------------------------------------------------------

  message = myNextion.listen(); //check for message
  if (message != "") { // if a message is received...

    //------------------------------------------------------------------------------------------
    //  buttons action Pump A
    //------------------------------------------------------------------------------------------

    //--------------      start A      -------------------------------------------------------

    if ((message == "65 0 5 1 ffff ffff ffff") && (digitalRead(stopa) == 1)) {
      if ((delaya > 0) && (delaya < 30240 / microsteps / gearratio)) {
        statea = 0;
        timestatea = 0;
        digitalWrite(enablea, HIGH);     //HIGH = disable
        myNextion.sendCommand("vis flowtooa,1");
        myNextion.setComponentValue("main.tooa", 1);
        myNextion.setComponentValue("main.runninga", 0);
      }
      else {
        statea = 1;
        timestatea = 1;
        myNextion.sendCommand("vis flowtooa,0");
        myNextion.sendCommand("vis stopa,1");  //show stopa button
        myNextion.setComponentValue("main.runninga", 1);
      }
    }

    //--------------       stop A      -------------------------------------------------------
    if (message == "65 0 a 1 ffff ffff ffff") {
      statea = 0;
      timestatea = 0;
      digitalWrite(enablea, HIGH);     //HIGH = disable
      myNextion.sendCommand("vis stopa,0");  //hide stopa button
      myNextion.setComponentValue("main.runninga", 0);
      myNextion.setComponentValue("main.n8", addedfina);
    }

    //--------------       reset volume A     -------------------------------------------------------
    if (message == "65 0 18 1 ffff ffff ffff") {
      addeda = 0;
      addedfina = 0;
      myNextion.setComponentValue("main.n8", addedfina);
    }
    
    //--------------       update volume A     -------------------------------------------------------
    if (message == "65 0 1 1 ffff ffff ffff") {
      myNextion.setComponentValue("main.n8", addedfina);
    }

    //--------------       flow A save      -------------------------------------------------------
    if (message == "65 1 2 1 ffff ffff ffff") {

      delay(600);
      flowa = myNextion.getComponentValue("flowa.ratea");
      flowdeza = myNextion.getComponentValue("flowa.ratedeza");
      diaa = myNextion.getComponentValue("syA.diaa");
      diadeza = myNextion.getComponentValue("syA.diadeza");

      radfina = (diaa * 1000 + diadeza * 10) / 2;  //radius *1000
      syringefactora = 1000000000000 / ((radfina) * (radfina) * PI); //syringefactor in µm/mL

      flowfina = flowa * 10 + flowdeza;
      delaya = ((factor / (syringefactora * flowfina / 10000)));

      myNextion.setComponentValue("main.n0", flowa);
      myNextion.setComponentValue("main.n2", flowdeza);

      if ((delaya > 0) && (delaya < 30240 / microsteps / gearratio)) {
        statea = 0;
        timestatea = 0;
        digitalWrite(enablea, HIGH);     //HIGH = disable
        myNextion.sendCommand("vis flowtooa,1");
        myNextion.setComponentValue("main.tooa", 1);
        myNextion.setComponentValue("main.runninga", 0);
      }
      else {
        myNextion.sendCommand("vis flowtooa,0");
      }

    }
    //--------------       flowadez save      -------------------------------------------------------
    if (message == "65 2 2 1 ffff ffff ffff") {
      delay (600);
      flowa = myNextion.getComponentValue("flowa.ratea");
      flowdeza = myNextion.getComponentValue("flowa.ratedeza");
      diaa = myNextion.getComponentValue("syA.diaa");
      diadeza = myNextion.getComponentValue("syA.diadeza");

      radfina = (diaa * 1000 + diadeza * 10) / 2;  //radius *1000
      syringefactora = 1000000000000 / ((radfina) * (radfina) * PI); //syringefactor in µm/mL

      flowfina = flowa * 10 + flowdeza;
      delaya = ((factor / (syringefactora * flowfina / 10000)));

      myNextion.setComponentValue("main.n0", flowa);
      myNextion.setComponentValue("main.n2", flowdeza);

      if ((delaya > 0) && (delaya < 30240 / microsteps / gearratio)) {
        statea = 0;
        timestatea = 0;
        digitalWrite(enablea, HIGH);     //HIGH = disable
        myNextion.sendCommand("vis flowtooa,1");
        myNextion.setComponentValue("main.tooa", 1);
        myNextion.setComponentValue("main.runninga", 0);
      }
      else {
        myNextion.sendCommand("vis flowtooa,0");
      }
    }
    //--------------       syA save      -------------------------------------------------------
    if (message == "65 5 2 1 ffff ffff ffff") {
      delay (600);
      flowa = myNextion.getComponentValue("flowa.ratea");
      flowdeza = myNextion.getComponentValue("flowa.ratedeza");
      diaa = myNextion.getComponentValue("syA.diaa");
      diadeza = myNextion.getComponentValue("syA.diadeza");

      radfina = (diaa * 1000 + diadeza * 10) / 2;  //radius *1000
      syringefactora = 1000000000000 / ((radfina) * (radfina) * PI); //syringefactor in µm/mL

      flowfina = flowa * 10 + flowdeza;
      delaya = ((factor / (syringefactora * flowfina / 10000)));
      
      myNextion.setComponentValue("main.n4", diaa);
      myNextion.sendCommand("main.t6.txt=syA.t13.txt");


      if ((delaya > 0) && (delaya < 30240 / microsteps / gearratio)) {
        statea = 0;
        timestatea = 0;
        digitalWrite(enablea, HIGH);     //HIGH = disable
        myNextion.sendCommand("vis flowtooa,1");
        myNextion.setComponentValue("main.tooa", 1);
        myNextion.setComponentValue("main.runninga", 0);
      }
      else {
        myNextion.sendCommand("vis flowtooa,0");
      }
    }

    //--------------       pressure A restart     -------------------------------------------------------

    if (message == "65 0 23 1 ffff ffff ffff") {

      toohigha = 0;
      myNextion.sendCommand("vis pressurea,0");
      myNextion.setComponentValue("main.presstooa", 0);
    }

    //--------------       manual stop A      -------------------------------------------------------
    if (message == "65 b 1 1 ffff ffff ffff") {
      statea = 0;
      timestatea = 0;
      digitalWrite(enablea, HIGH);     //HIGH = disable
      pulla = 0;
      pusha = 0;
      i = 0; j = 0;
    }

    //--------------      manual A pull touch    -------------------------------------------------------
    if (message == "65 b 3 1 ffff ffff ffff") {
      statea = 0;
      timestatea = 0;
      pusha = 0;
      pulla = 1;
      stepsa = 8000 * microsteps * gearratio; //maximal pull ditance = 60 mm  // steps per mm: 133 (without gear and microsteps)
    }
    //--------------       manual A pull release      -------------------------------------------------------
    if (message == "65 b 3 0 ffff ffff ffff") {
      pulla = 0;
    }

    //--------------       // manual A push touch      -------------------------------------------------------
    if (message == "65 b 4 1 ffff ffff ffff") {
      statea = 0;
      timestatea = 0;
      pulla = 0;
      pusha = 1;
      stepsa = 8000 * microsteps * gearratio; //maximal pull ditance = 60 mm = 216000
    }
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

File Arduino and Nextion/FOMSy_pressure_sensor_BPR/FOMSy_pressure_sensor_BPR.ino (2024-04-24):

#include <Nextion.h>          // Nextion Library by Bentley Born https://github.com/bborncr/nextion
#include <SoftwareSerial.h>   // Software Serial Port (included in Arduino IDE "no download")
SoftwareSerial nextion(10, 11);// Nextion (TX, RX)
Nextion myNextion(nextion, 9600); // Setup of Nextion library with name NextionLCD at 9600bps

#define pina A0
#define pinb A1
#define tooa 7
#define toob 8
int buttonred = 2;
int buttongreen = 3;
int buttongreenstate = 0;
int buttonredstate = 0;
int rawa = 0;
int rawb = 0;
float bara = 0;
float barb = 0;
float maxa = 10;
float maxb = 10;
float cala = 0;
float calb = 0;
int statecal = 0;
unsigned long senda = 0;
unsigned long sendgrapha = 0;
unsigned long sendb = 0;
unsigned long sendgraphb = 0;
byte statea = 0;
byte stateb = 0;
byte maxmenua = 0;
byte maxmenub = 0;
//motor pins
int enA = 4;
int motorin1 = 5;
int motorin2 = 6;
String message;   // received message for Nextion LCD

void setup()
{
  digitalWrite(pina, HIGH); // turn on pullup resistors
  digitalWrite(pinb, HIGH); // turn on pullup resistors
  pinMode(tooa, OUTPUT);
  pinMode(toob, OUTPUT);
  pinMode(buttonred, INPUT_PULLUP);
  pinMode(buttongreen, INPUT_PULLUP);

  pinMode(enA, OUTPUT);
  pinMode(motorin1, OUTPUT);
  pinMode(motorin2, OUTPUT);

  myNextion.init();
  nextion.begin(9600); // open the serial port at 115200 bps:
}

void loop() {
  //------------------------------------------------------------------------------------------
  //  buttons action
  //------------------------------------------------------------------------------------------

  //--------------       button green pressed      -------------------------------------------------------

  if (digitalRead(buttongreen) == LOW) { //LOW = button pressed
    buttongreenstate = 1;
  } else {
    buttongreenstate = 0;
  }

  //--------------       button red pressed      -------------------------------------------------------

  if (digitalRead(buttonred) == LOW) { //LOW = button pressed
    buttonredstate = 1;
  } else {
    buttonredstate = 0;
  }

  //--------------------------- motor spins clockwise = increase pressure on BPR-----------------------------

  if (buttongreenstate == 1) {

    digitalWrite(motorin1, HIGH);
    digitalWrite(motorin2, LOW);
    digitalWrite(enA, 255);
  }

  //--------------------------- motor spins counterclockwise = decrease pressure on BPR-----------------------------

  if (buttonredstate == 1) {

    digitalWrite(motorin1, LOW);
    digitalWrite(motorin2, HIGH);
    digitalWrite(enA, 255);
  }

  //--------------------------- motor stops-----------------------------

  if (buttonredstate == 0 && buttongreenstate == 0) {

    digitalWrite(motorin1, LOW);
    digitalWrite(motorin2, LOW);
  }
  if (buttonredstate == 1 && buttongreenstate == 1) {

    digitalWrite(motorin1, LOW);
    digitalWrite(motorin2, LOW);
  }

  //--------------       nextion actions      -------------------------------------------------------


  message = myNextion.listen(); //check for message
  if (message != "") { // if a message is received...

    //--------------       start A      -------------------------------------------------------

    if (message == "65 0 4 1 ffff ffff ffff") {
      statea = 1;
      myNextion.sendCommand("vis stopa,1");  //show stopa button
      myNextion.sendCommand("va0.val=1");
    }
    //--------------       stop A      -------------------------------------------------------

    if (message == "65 0 12 1 ffff ffff ffff") {
      statea = 0;
      myNextion.sendCommand("vis stopa,0");  //hide stopa button
      myNextion.sendCommand("va0.val=0");
    }

    //--------------       reset A      -------------------------------------------------------

    if (message == "65 0 5 1 ffff ffff ffff") {
      myNextion.sendCommand("cle 1,0");
      myNextion.sendCommand("cle 1,2");
    }

    //--------------       start B      -------------------------------------------------------

    if (message == "65 0 6 1 ffff ffff ffff") {
      stateb = 1;
      myNextion.sendCommand("vis stopb,1");  //show stopa button
      myNextion.sendCommand("va1.val=1");
    }

    //--------------       stop B      -------------------------------------------------------

    if (message == "65 0 13 1 ffff ffff ffff") {
      stateb = 0;
      myNextion.sendCommand("vis stopb,0");  //hide stopa button
      myNextion.sendCommand("va1.val=0");
    }

    //--------------       reset B      -------------------------------------------------------

    if (message == "65 0 7 1 ffff ffff ffff") {
      myNextion.sendCommand("cle 1,1");
      myNextion.sendCommand("cle 1,3");
    }

    //--------------       save max B      -------------------------------------------------------
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
